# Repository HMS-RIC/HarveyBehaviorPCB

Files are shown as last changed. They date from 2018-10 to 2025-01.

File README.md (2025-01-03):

# HarveyBehaviorPCB v2
Circuit board for Harvey Lab VR behavior rigs

## Features
This board is designed to integrate a Teensy microcontroller and a National Instruments DAQ board (NI USB-600x) with the sensors and actuators on the behavior rig. Importantly, the board is used to convey the spherical treadmill movement signals to the VR computer. The Teensy makes a digital connection to the two ball movement sensors (mounted on the base of the spherical treadmill) to make continuous reading of ball movement. It then produces three analog outputs, representing velocity in the _Yaw_, _Pitch_, and _Roll_ axes, that are read into the VR computer by the DAQ board.

Other optional features of the PCB are: 
- Driver circuit for 2 solenoid valves (e.g. for liquid rewards)
- Two lick detector circuits
- A photodiode amplifier
- Many expansion ports/connectors: BNC connections, 0.1" headers, and a serial I2C connection (Qwiic connector)

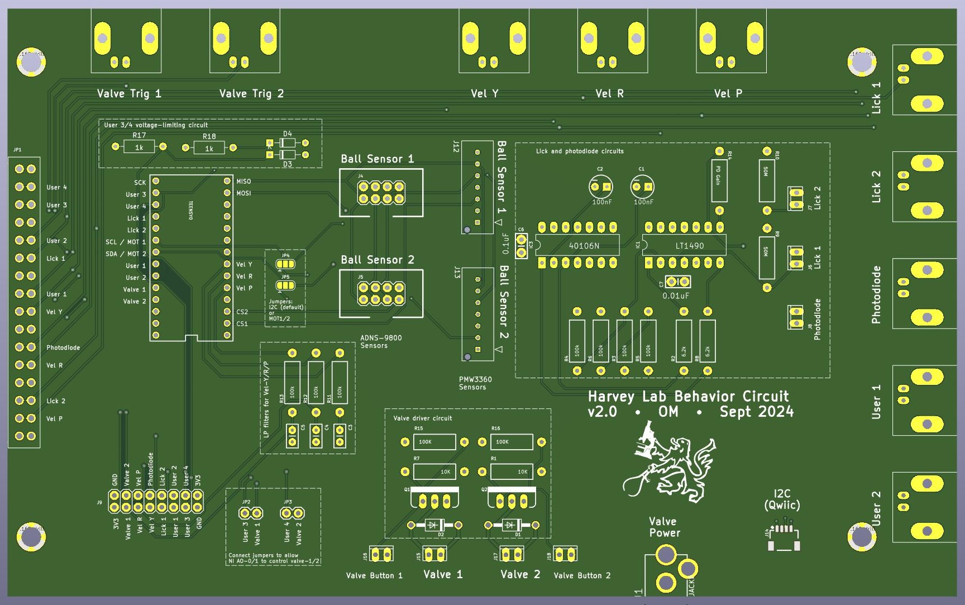
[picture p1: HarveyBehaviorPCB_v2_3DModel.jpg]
3D PCB model


## Fabrication
The full fabrication design is included in the [Gerber Zip File](PCB_v2_KiCAD/Gerbers/HarveyBehaviorPCB_v2.zip?raw=true). You can upload this file to any PCB fabricator to get a quote and place an order. (The board does not have any special features, so the default settings for PCB manufacture are probably fine.) One a relatively low-cost option for a board this size is the $33/board (3 board minimum) special at [Advanced Circuits](https://www.advancedpcb.com/en-us/33-each-special/).

## Assembly
The [Bill of Materials](HarveyBehaviorPCB_v2_BOM.xlsx?raw=true) (BOM) file has the full list of components. Everything but the optional I2C connector is a through-hole part and can be soldered on with a simple soldering iron (and [proper technique](https://mightyohm.com/files/soldercomic/FullSolderComic_EN.pdf)). The board is divided up into labeled regions that describe their high-level function and allow you to populate only the subset of components that you plan to use:
- **Ball sensor connectors**: The board is designed to work with two types of ball sensor ([ADNS-9800](https://www.tindie.com/products/citizenjoe/adns-9800-motion-sensor/) and [PMW3360](https://www.tindie.com/products/citizenjoe/pmw3360-motion-sensor/)). Chose one and populate the appropriate connector. (Also be sure to use the correct Teensy firmware for your ball sensor.)
- **Valve driver circuit**, **Lick and photodiode circuits**: These are optional functionalities. Only populate these regions if you plan to use them.
- **LP filters for velocity signals**: These are not optional. They low-pass filter the Teensy's digital (PWM) output to form a smooth analog signal for the NI board to acquire.
- **User 3/4 voltage-limiting circuit**: This is necessary if you plan to use the NI board's analog output pins (_AO-0_, _AO-1_) to control the voltage on _User-3_ and _User-4_. This circuit protects the Teensy from an accidental +5V output from the NI board (since the Teensy 4.0 cannot handle >3.3V inputs).
- **Jumpers JP2, JP3**: Optional. Short these jumpers (i.e., connect the pins within each jumper) to enable the NI analog output (_AO-0/1_, a.k.a. _User-3/4_) to control the valves.
- **Jumpers JP4, JP5**: Optional. In their default state they enable the I2C connector and disable the _MOT1_/_MOT2_ connections to the ball sensors. The _MOTx_ lines are not used during typical operation, so these jumpers are unlikely to be used.

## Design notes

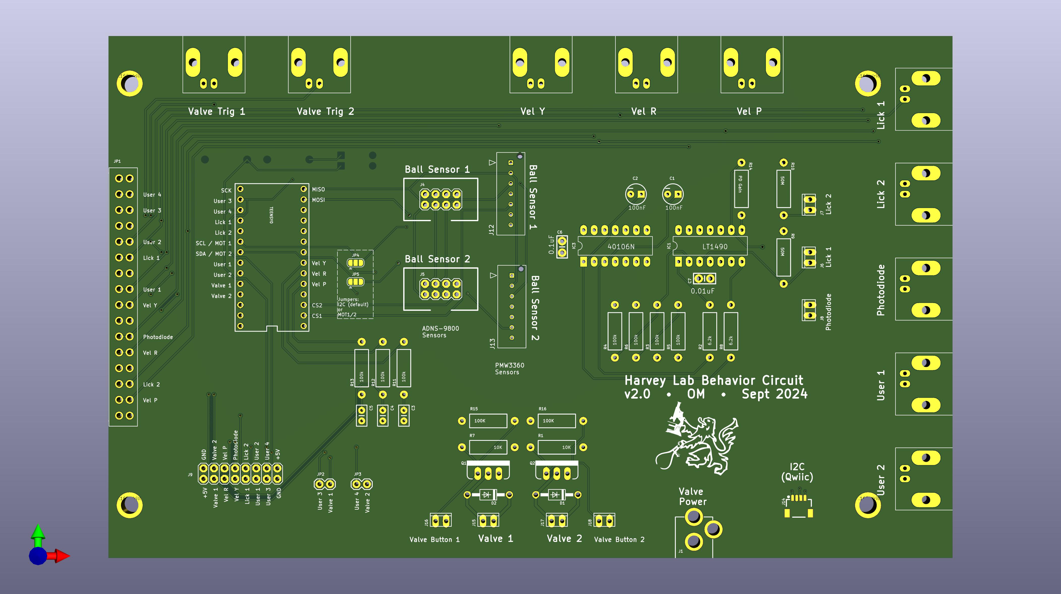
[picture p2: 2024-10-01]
PCB_v2_KiCAD/HarveyBehaviorPCB_v2.jpg

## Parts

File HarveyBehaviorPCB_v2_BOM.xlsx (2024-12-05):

Part | Value | Qty | Device | Digikey Part # | Unit Price | Total Price | Description | Notes
C1,C2 | 100nF | 2 |  |  |  | $0.00
C3-5 | 0.22uF | 3 |  |  |  | $0.00
C6 | 0.1uF | 1 |  |  |  | $0.00
C7 | 0.01uF | 1 |  |  |  | $0.00
D1,D2 | 1N4148 | 2 | Diode (1N58) | 497-7053-1-ND | $0.39 | $0.78
D3,D4 | Vz=3V3 | 2 | Zener diode, Vz=3.6V | 1727-6244-1-ND | $0.10 | $0.20
IC1 | LT1490A | 1 | LT1490A | LT1491ACN#PBF-ND | $6.41 | $6.41 | Quad OP AMP
IC3 | 40106N | 1 | 40106 | 296-3503-5-ND | $0.51 | $0.51 | Hex SCHMITT TRIGGER
J1 |  | 1 | PJ-202A | CP-202A-ND | $0.61 | $0.61
J4,J5 |  | 2 | Shrouded 2x4 header | 609-3530-ND | $0.76 | $1.52 | Connector to ADNS-9800 ball sensor | Pick only one connector type based on ball sensor model
J12,J13 |  | 2 | 1x7 connector | 900-0534760710-ND | $0.73 | $1.46 | Connector to PMW3360 ball sensor
J6-8,J15-18 | MTA02-100 | 7 | 1x2 connector | A19423-ND | $0.11 | $0.77 |  | Or any other 1x02 connector with 0.1" spacing
J9 | M08X2 | 1 | 2x8 header | 609-3220-ND | $0.60 | $0.60 |  | (or equivalent part)
J14 |  | 1 | JST SH/SR 4pos 1mm connector | 455-SM04B-SRSS-TBCT-ND | $0.71 | $0.71 | Qwiic/I2C Connector
JP1 | M16 | 1 | Connector to DAQ | 277-6221-ND | $17.34 | $17.34 | Connector to Ni USB-600x DAQ board
JP2,JP3 |  | 2 | JUMPER-2PTH | 952-2262-ND | $0.60 | $1.20 |  | also need jumper cap (e.g.,S9337-ND)
Q1,Q2 |  | 2 | nFET Transistor | 568-7512-5-ND | $2.20 | $4.40
R1,R7 | 10k | 2 | Standard (Axial) Resistor |  |  | $0.00
R2,R8 | 6.2k | 2 | Standard (Axial) Resistor |  |  | $0.00
R3-6, R11-13 | 100k | 7 | Standard (Axial) Resistor |  |  | $0.00
R9,R10 | 50M | 2 | Standard (Axial) Resistor |  |  | $0.00
R14 |  | 1 | Standard (Axial) Resistor |  |  | $0.00 |  | Chose value based on desired PD Gain
R15,R16 | 100K | 2 | Standard (Axial) Resistor |  |  | $0.00
R17,R18 | 1k | 2 | Standard (Axial) Resistor |  |  | $0.00
TEENSY0 |  | 1 | Teensy 3.2 or 4.0 |  |  | $0.00
U$1-10 |  | 10 | BNC Connector | WM5514-ND | $1.48 | $14.80
 |  |  | Additional conponents not on the PCB
 |  | 2 | Molex 0151370706 | WM25326-ND | $6.32 | $12.64 | Cable for PMW3360 ball sensor
 |  | 2 | Molex 0534260710 | WM14653-ND | $0.56 | $1.12 | Connector to be soldered to PMW3360 ball sensor

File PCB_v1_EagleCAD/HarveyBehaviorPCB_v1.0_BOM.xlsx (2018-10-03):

Part | Value | Device | Package | Description
C1 | 100nF
C2 | 100nF
C3 | 0.22uF
C4 | 0.22uF
C5 | 0.22uF
C6 | 0.1uF
C7 | 0.01uF
D1 | 1N4148 | 1N4004 |  | DIODE
D2 | 1N4148 | 1N4004 |  | DIODE
IC1 | LT1490A |  |  | Quad Wideband, Low Power Current Feedback OP AMP
IC3 | 40106N |  |  | Hex SCHMITT TRIGGER
J1 |  |  |  | Power Jack
J2 |  | M01SMTSO-256-ET-0.165DIA | SMTSO-256-ET-0.165DIA | Header 1
J3 |  | M01SMTSO-256-ET-0.165DIA | SMTSO-256-ET-0.165DIA | Header 1
J4 | BALL_1 | M04X2 | 2X4 | .1 header | two rows of four."
J5 | BALL_2 | M04X2 | 2X4 | .1 header | two rows of four."
J6 |  | MTA02-100 | 10X02MTA | AMP connector
J7 |  | MTA02-100 | 10X02MTA | AMP connector
J8 | Photodiode | MTA02-100 | 10X02MTA | AMP connector
J9 |  | M08X2 | 2X8 | .1 headers | two rows of 8 each"
J10 |  | M01SMTSO-256-ET-0.165DIA | SMTSO-256-ET-0.165DIA | Header 1
J11 |  | M01SMTSO-256-ET-0.165DIA | SMTSO-256-ET-0.165DIA | Header 1
J15 | Valve 1 | MTA02-100 | 10X02MTA | AMP connector
J16 | Valve 1 Switch | MTA02-100 | 10X02MTA | AMP connector
J17 | Valve 2 | MTA02-100 | 10X02MTA | AMP connector
J18 | Valve 2 Switch | MTA02-100 | 10X02MTA | AMP connector
JP1 | M16 | M16 | 1X16_TERM_BLOCK_0.15",1x16 .1" header"
Q1 | MOSFET-NCHANNELFQP30N06L |  | TO220V | Common NMOSFET Parts
Q2 | MOSFET-NCHANNELFQP30N06L |  | TO220V | Common NMOSFET Parts
R1 | 10K |  |  | Resistor
R2 | 6.2k |  |  | Resistor
R3 | 100k |  |  | Resistor
R4 | 100k |  |  | Resistor
R5 | 100k |  |  | Resistor
R6 | 100k |  |  | Resistor
R7 | 10K |  |  | Resistor
R8 | 6.2k |  |  | Resistor
R9 | 50M |  |  | Resistor
R10 | 50M |  |  | Resistor
R11 | 100k |  |  | Resistor
R12 | 100k |  |  | Resistor
R13 | 100k |  |  | Resistor
R14 | PD Gain |  |  | Resistor
TEENSY | TEENSY_3.1-3.2_DIL | TEENSY_3.1-3.2_DIL | TEENSY_3.0-3.2&LC_DIL | Teensy 3.1 or 3.2 in a DIL Layout.
U$1 | BNCPTH | BNCPTH | BNC | BNC Connector, Mouser Part# 5227161
U$2 | BNCPTH | BNCPTH | BNC | BNC Connector, Mouser Part# 5227161
U$3 | BNCPTH | BNCPTH | BNC | BNC Connector, Mouser Part# 5227161
U$4 | BNCPTH | BNCPTH | BNC | BNC Connector, Mouser Part# 5227161
U$5 | BNCPTH | BNCPTH | BNC | BNC Connector, Mouser Part# 5227161
U$6 | BNCPTH | BNCPTH | BNC | BNC Connector, Mouser Part# 5227161
U$7 | BNCPTH | BNCPTH | BNC | BNC Connector, Mouser Part# 5227161
U$8 | BNCPTH | BNCPTH | BNC | BNC Connector, Mouser Part# 5227161
U$9 | BNCPTH | BNCPTH | BNC | BNC Connector, Mouser Part# 5227161
U$10 | BNCPTH | BNCPTH | BNC | BNC Connector, Mouser Part# 5227161

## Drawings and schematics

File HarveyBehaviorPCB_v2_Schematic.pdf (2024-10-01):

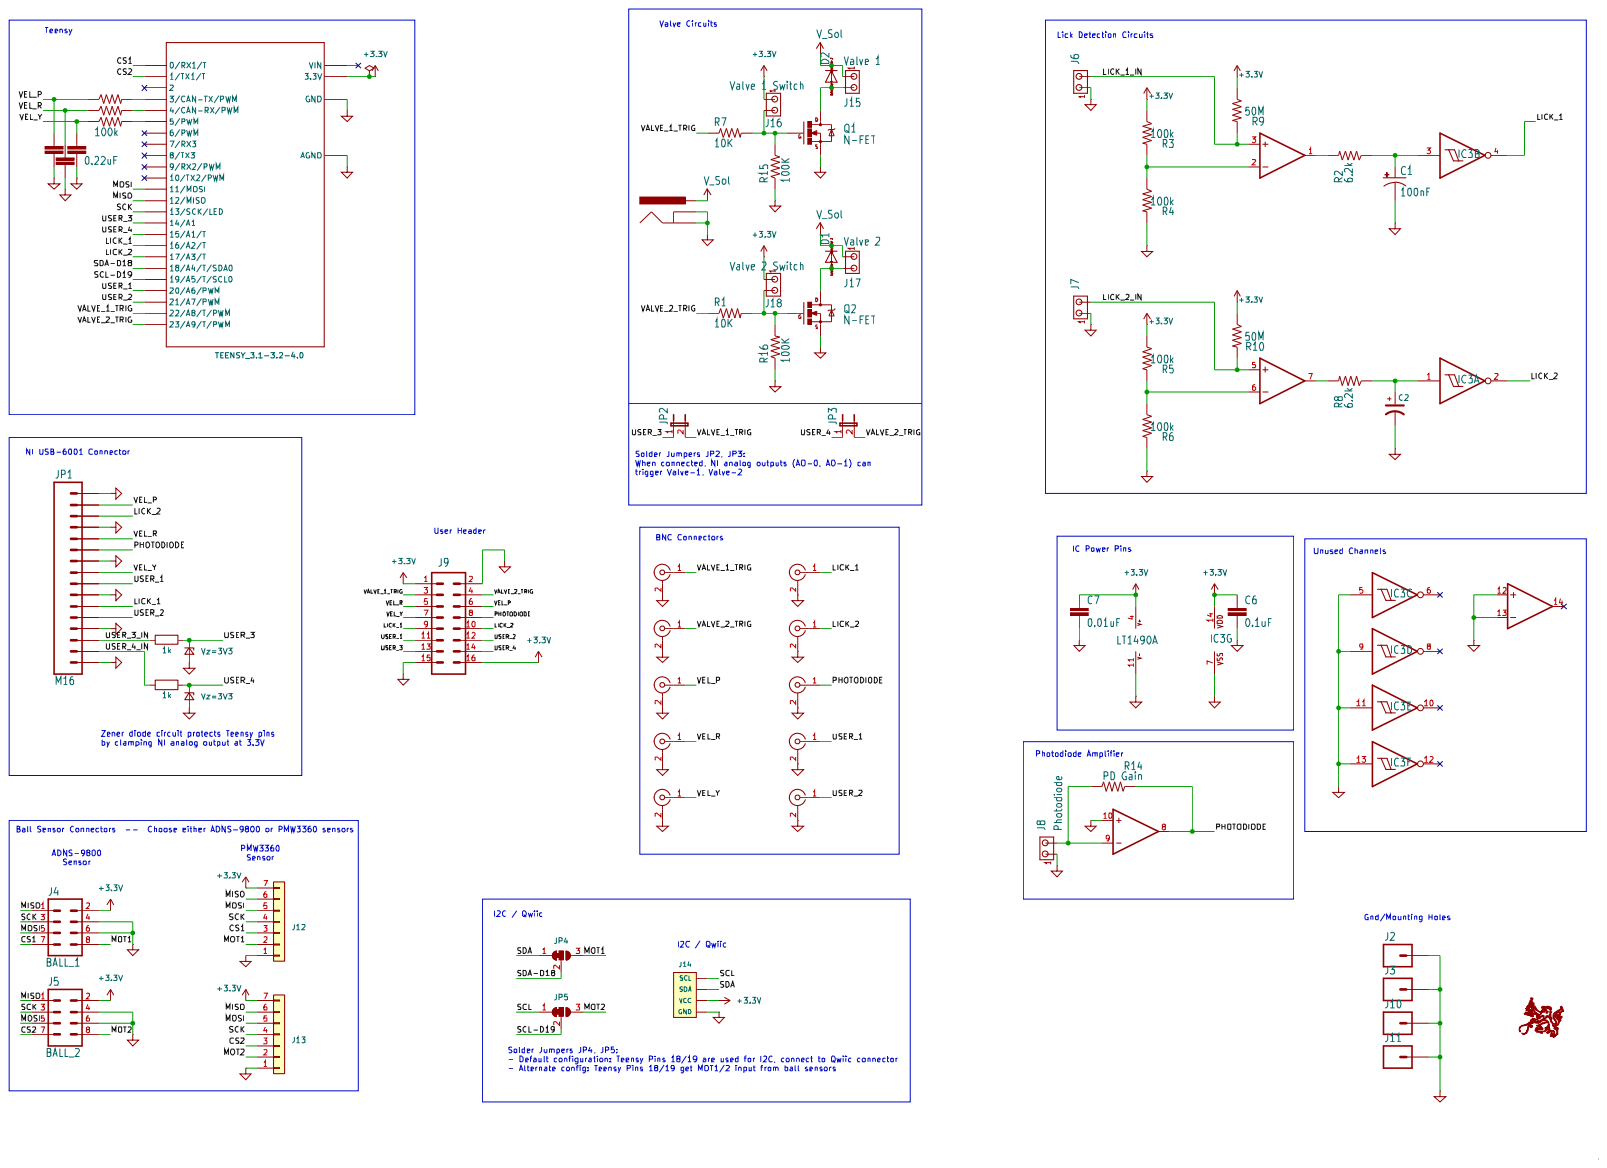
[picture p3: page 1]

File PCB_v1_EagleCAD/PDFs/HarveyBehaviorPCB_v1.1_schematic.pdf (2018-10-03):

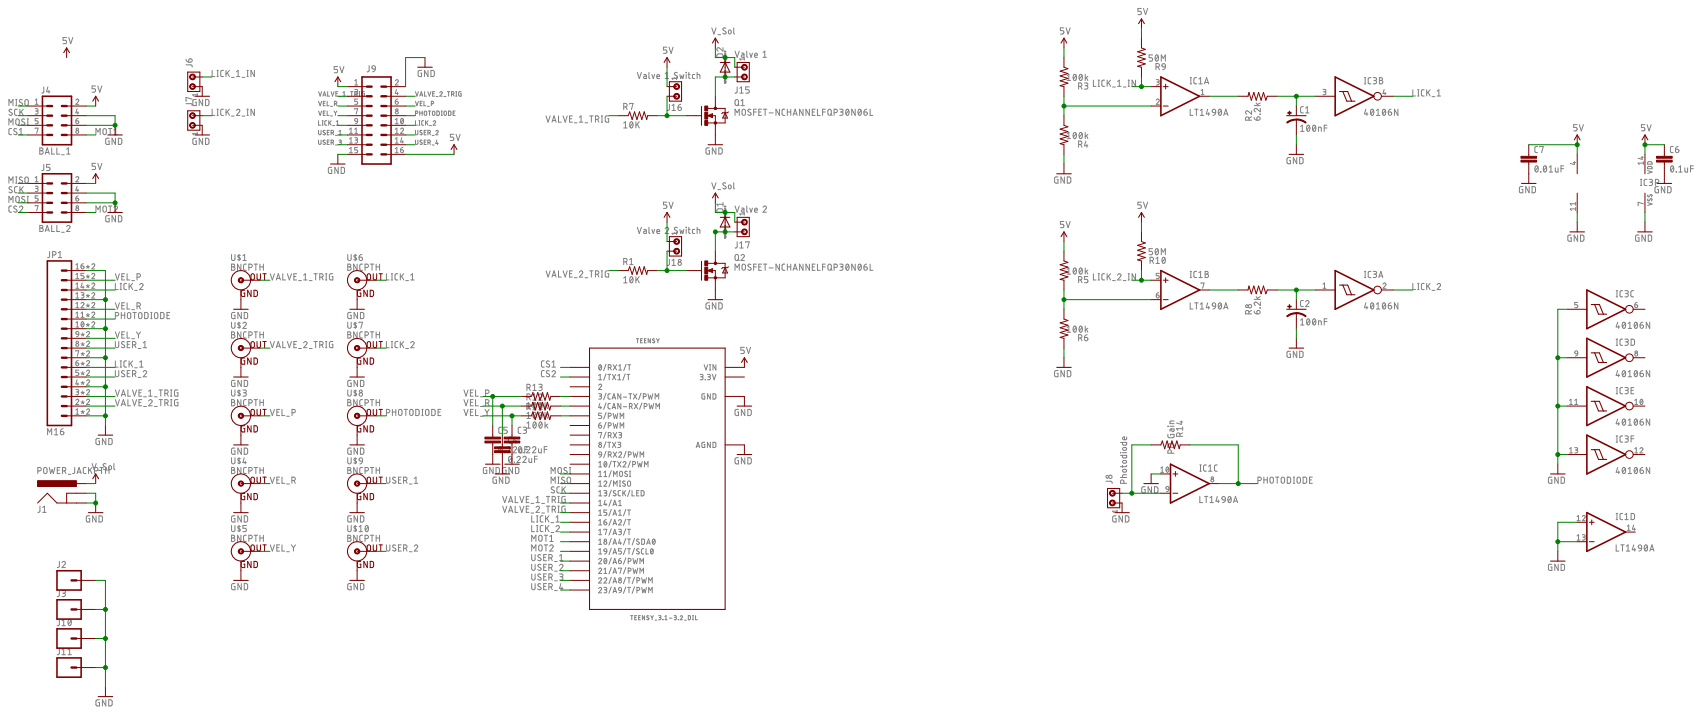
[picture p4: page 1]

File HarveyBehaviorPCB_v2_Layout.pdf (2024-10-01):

1 | 2 | 3 | 4 | 5

A

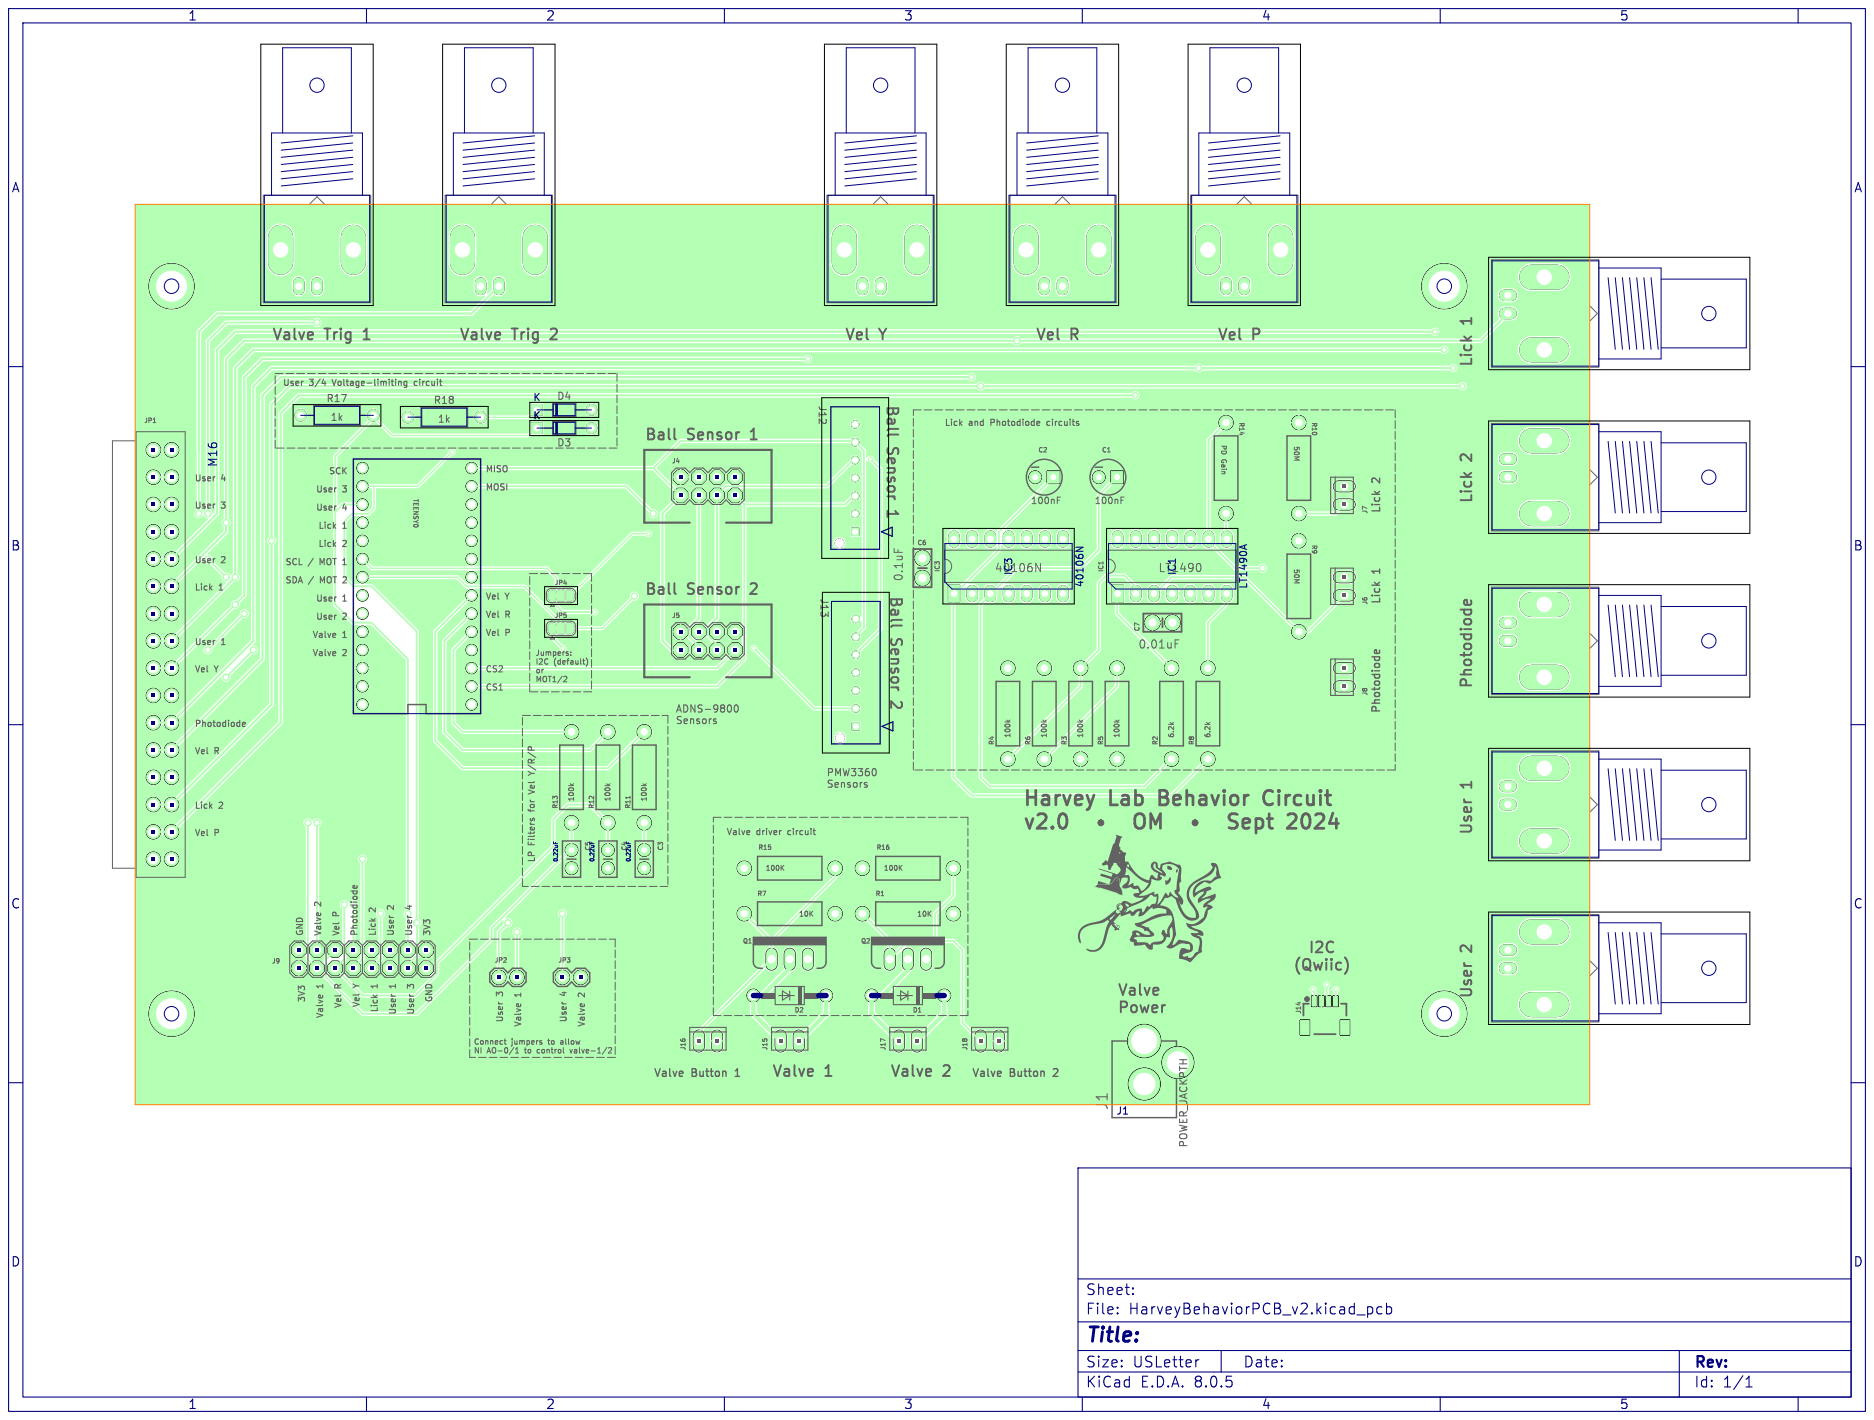
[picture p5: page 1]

Id: 1/1 Title: File: HarveyBehaviorPCB_v2.kicad_pcb Sheet:

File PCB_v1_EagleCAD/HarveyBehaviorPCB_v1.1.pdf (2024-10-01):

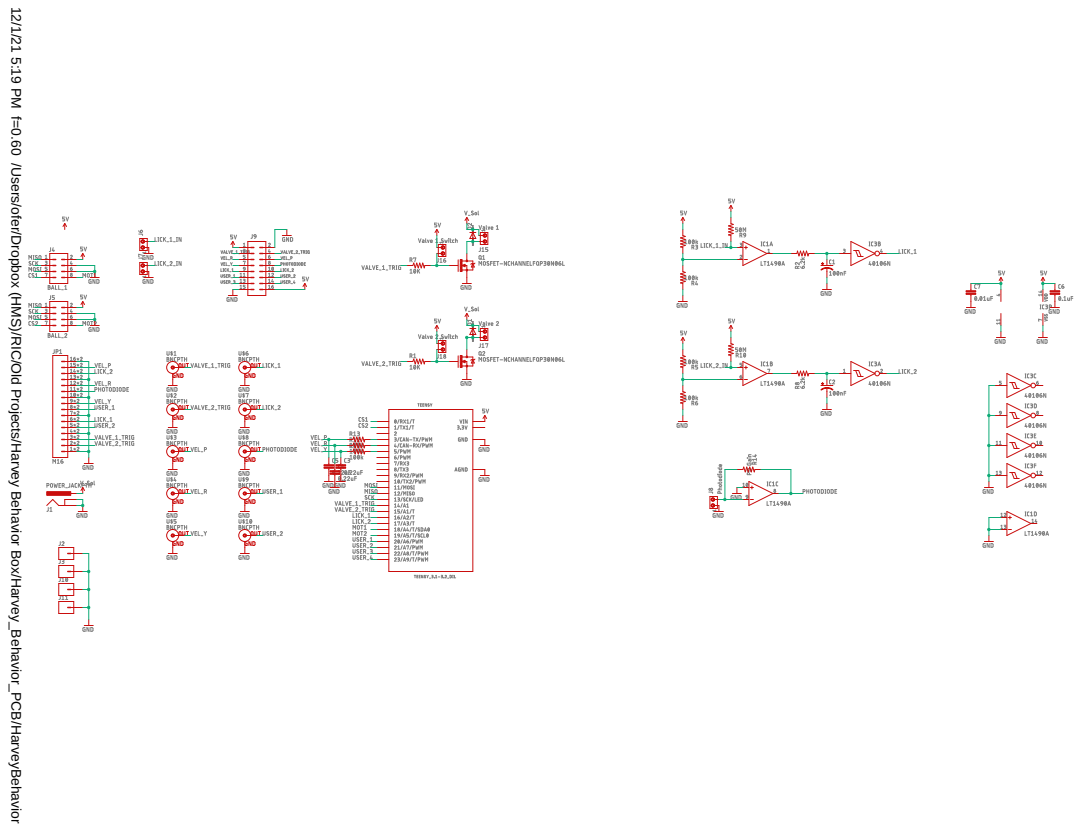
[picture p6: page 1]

12/1/21 5:19 PM f=0.60 /Users/ofer/Dropbox (HMS)/RIC/Old Projects/Harvey Behavior Box/Harvey_Behavior_PCB/HarveyBehaviorPCB_v1.1.sch (Sheet: 1/1)

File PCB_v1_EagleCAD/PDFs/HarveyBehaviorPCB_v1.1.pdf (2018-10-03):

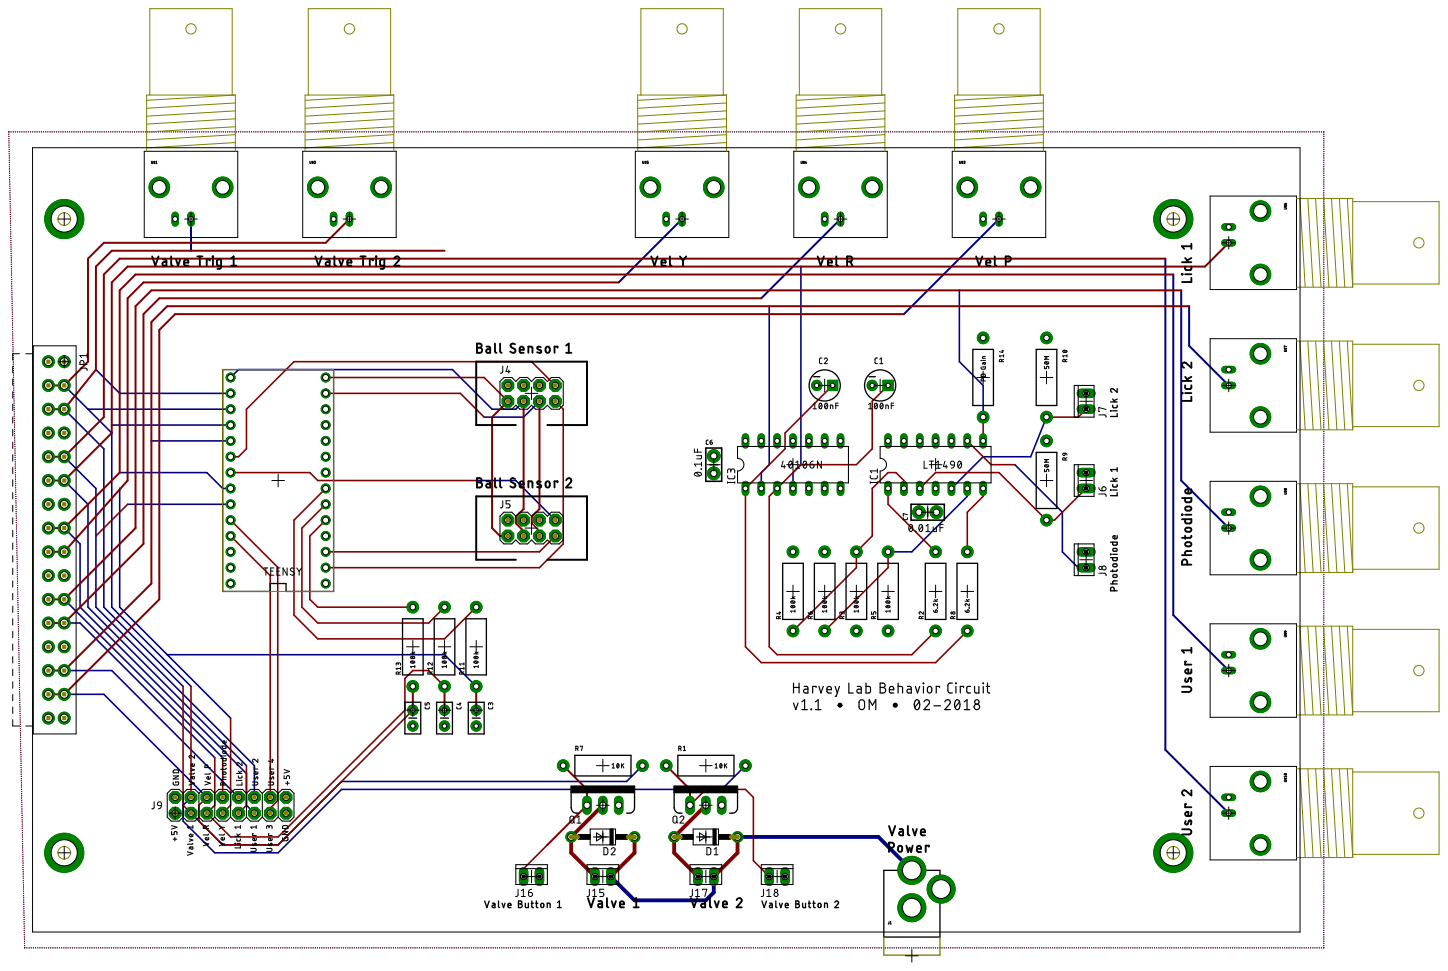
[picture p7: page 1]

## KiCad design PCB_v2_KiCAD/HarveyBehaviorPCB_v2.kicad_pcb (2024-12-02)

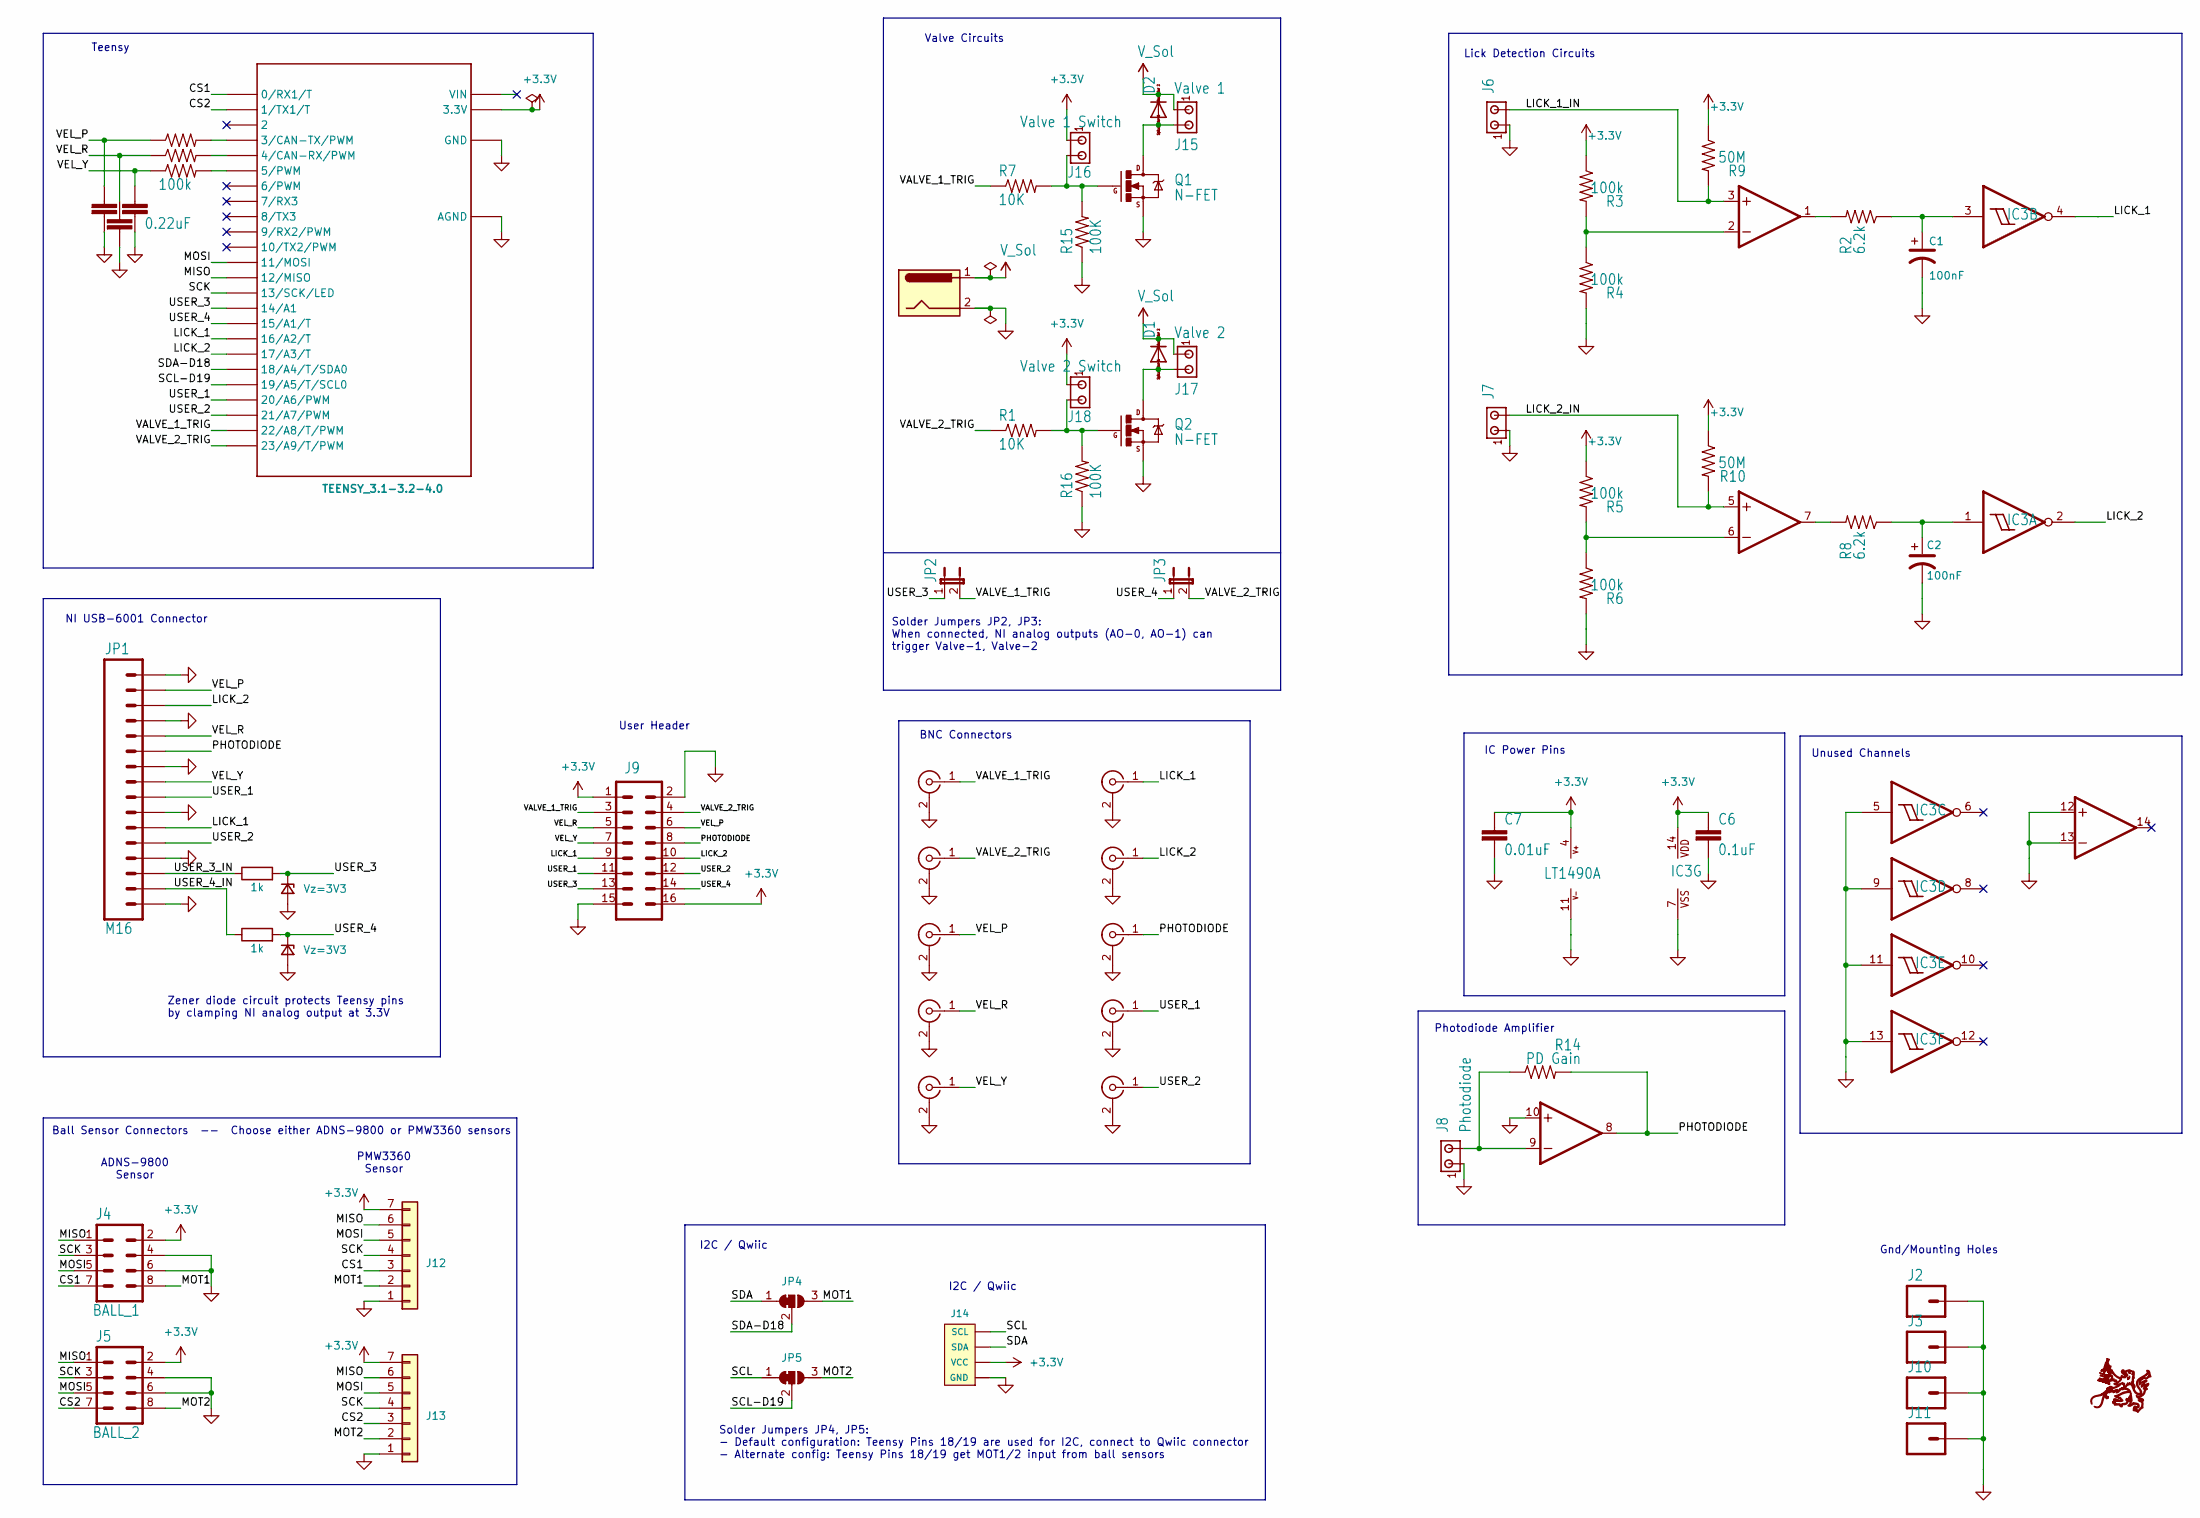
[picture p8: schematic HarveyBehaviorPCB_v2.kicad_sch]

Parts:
C1, C2: 100nF; CPOL-RADIAL-10UF-25V
C3, C4, C5: 0.22uF; CAP-PTH-SMALL2
C6: 0.1uF; CAP-PTH-SMALL-KIT
C7: 0.01uF; CAP-PTH-SMALL-KIT
D1, D2: 1N4148; DO41-10
D3, D4: Vz=3V3; D_DO-34_SOD68_P7.62mm_Horizontal
IC1: LT1490A; DIP-14_W7.62mm_LongPads
IC3: 40106N; DIP-14_W7.62mm_LongPads
J1: POWER_JACKPTH; POWER_JACK_PTH
J2, J3, J10, J11: M01SMTSO-256-ET-0.165DIA; SMTSO-256-ET-0.165DIA
J4: BALL_1; 2X4
J5: BALL_2; 2X4
J6, J7: MTA02-100; 10X02MTA
J8: Photodiode; 10X02MTA
J9: M08X2; 2X8
J12, J13: Conn_01x07; CON_535170730_MOL
J14: I2C_STANDARDQWIIC; 1X04_1MM_RA
J15: Valve 1; 10X02MTA
J16: Valve 1 Switch; 10X02MTA
J17: Valve 2; 10X02MTA
J18: Valve 2 Switch; 10X02MTA
JP1: M16; 1X16_TERM_BLOCK_0.15_
JP2, JP3: JUMPER-2PTH; 1X02
JP4, JP5: SolderJumper_3_Bridged12; SolderJumper-3_P1.3mm_Bridged12_RoundedPad1.0x1.5mm
Q1, Q2: N-FET; TO220V
R1, R7: 10K; AXIAL-0.5
R2, R8: 6.2k; AXIAL-0.5
R3, R4, R5, R6, R11, R12, R13: 100k; AXIAL-0.5
R9, R10: 50M; AXIAL-0.5
R14: PD Gain; AXIAL-0.5
R15, R16: 100K; AXIAL-0.5
R17, R18: 1k; R_Axial_DIN0207_L6.3mm_D2.5mm_P10.16mm_Horizontal
TEENSY0: TEENSY_3.1-3.2-4.0; TEENSY_3.0-3.2&LC_DIL
U$1, U$2, U$3, U$4, U$5, U$6, U$7, U$8, U$9, U$10: BNCPTH; BNC_Amphenol_B6252HB-NPP3G-50_Horizontal

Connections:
+3.3V: C6.1, C7.1, IC1.4 (V+), IC3.14 (VDD), J4.2, J5.2, J9.1, J9.16, J12.7, J13.7, J14.2 (VCC), J16.1, J18.1, R3.P$1 (1), R5.P$1 (1), R9.P$1 (1), R10.P$1 (1), TEENSY0.3.3V
/CS1: J4.7, J12.3, TEENSY0.0 (0/RX1/T)
/CS2: J5.7, J13.3, TEENSY0.1 (1/TX1/T)
/LICK_1: IC3.4 (O), J9.9, JP1.6, JP1.22 (6), TEENSY0.16/A2 (16/A2/T), U$6.1 (In)
/LICK_1_IN: IC1.3 (+IN), J6.2, R9.P$2 (2)
/LICK_2: IC3.2 (O), J9.10, JP1.14, JP1.30 (14), TEENSY0.17/A3 (17/A3/T), U$7.1 (In)
/LICK_2_IN: IC1.5 (+IN), J7.2, R10.P$2 (2)
/MISO: J4.1, J5.1, J12.6, J13.6, TEENSY0.12 (12/MISO)
/MOSI: J4.5, J5.5, J12.5, J13.5, TEENSY0.11 (11/MOSI)
/MOT1: J4.8, J12.2, JP4.3 (B)
/MOT2: J5.8, J13.2, JP5.3 (B)
/PHOTODIODE: IC1.8 (OUT), J9.8, JP1.11, JP1.27 (11), R14.P$2 (2), U$8.1 (In)
/SCK: J4.3, J5.3, J12.4, J13.4, TEENSY0.13 (13/SCK/LED)
/SCL: J14.4 (SCL), JP5.1 (A)
/SCL-D19: JP5.2 (C), TEENSY0.19/A5 (19/A5/T/SCL0)
/SDA: J14.3 (SDA), JP4.1 (A)
/SDA-D18: JP4.2 (C), TEENSY0.18/A4 (18/A4/T/SDA0)
/USER_1: J9.11, JP1.8, JP1.24 (8), TEENSY0.20/A6 (20/A6/PWM), U$9.1 (In)
/USER_2: J9.12, JP1.5, JP1.21 (5), TEENSY0.21/A7 (21/A7/PWM), U$10.1 (In)
/USER_3: D4.1 (K), J9.13, JP2.1, R18.2, TEENSY0.14/A0 (14/A1)
/USER_3_IN: JP1.3, JP1.19 (3), R18.1
/USER_4: D3.1 (K), J9.14, JP3.1, R17.2, TEENSY0.15/A1 (15/A1/T)
/USER_4_IN: JP1.2, JP1.18 (2), R17.1
/VALVE_1_TRIG: J9.3, JP2.2, R7.P$1 (1), TEENSY0.22/A8 (22/A8/T/PWM), U$1.1 (In)
/VALVE_2_TRIG: J9.4, JP3.2, R1.P$1 (1), TEENSY0.23/A9 (23/A9/T/PWM), U$2.1 (In)
/VEL_P: C5.1, J9.6, JP1.15, JP1.31 (15), R13.P$1 (1), U$3.1 (In)
/VEL_R: C4.1, J9.5, JP1.12, JP1.28 (12), R12.P$1 (1), U$4.1 (In)
/VEL_Y: C3.1, J9.7, JP1.9, JP1.25 (9), R11.P$1 (1), U$5.1 (In)
GND: C1.2 (-), C2.2, C3.2, C4.2, C5.2, C6.2, C7.2, D3.2 (A), D4.2 (A), IC1.10 (+IN), IC1.11 (V-), IC1.12 (+IN), IC1.13 (-IN), IC3.5 (I), IC3.7 (VSS), IC3.9 (I), IC3.11 (I), IC3.13 (I), J1.2, J2.P$1 (1), J3.P$1 (1), J4.4, J4.6, J5.4, J5.6, J6.1, J7.1, J8.1, J9.2, J9.15, J10.P$1 (1), J11.P$1 (1), J12.1, J13.1, J14.1 (GND), JP1.1, JP1.4, JP1.7, JP1.10, JP1.13, JP1.16, JP1.17 (1), JP1.20 (4), JP1.23 (7), JP1.26 (10), JP1.29 (13), JP1.32 (16), Q1.3 (S), Q2.3 (S), R4.P$2 (2), R6.P$2 (2), R15.P$1 (1), R16.P$1 (1), TEENSY0.AGND, TEENSY0.GND, U$1.2 (Ext), U$2.2 (Ext), U$3.2 (Ext), U$4.2 (Ext), U$5.2 (Ext), U$6.2 (Ext), U$7.2 (Ext), U$8.2 (Ext), U$9.2 (Ext), U$10.2 (Ext)
unnamed: C1.1 (+), IC3.3 (I), R2.P$1 (1)
unnamed: IC1.2 (-IN), R3.P$2 (2), R4.P$1 (1)
unnamed: IC1.1 (OUT), R2.P$2 (2)
unnamed: IC1.6 (-IN), R5.P$2 (2), R6.P$1 (1)
unnamed: IC1.7 (OUT), R8.P$2 (2)
unnamed: IC1.9 (-IN), J8.2, R14.P$1 (1)
unnamed: C2.1, IC3.1 (I), R8.P$1 (1)
unnamed: D2.A, J15.2, Q1.2 (D)
unnamed: J16.2, Q1.1 (G), R7.P$2 (2), R15.P$2 (2)
unnamed: D1.A, J17.2, Q2.2 (D)
unnamed: J18.2, Q2.1 (G), R1.P$2 (2), R16.P$2 (2)
unnamed: R11.P$2 (2), TEENSY0.5 (5/PWM)
unnamed: R12.P$2 (2), TEENSY0.4 (4/CAN-RX/PWM)
unnamed: R13.P$2 (2), TEENSY0.3 (3/CAN-TX/PWM)
V_Sol: D1.C, D2.C, J1.1, J15.1, J17.1

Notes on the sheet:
NI USB-6001 Connector
Zener diode circuit protects Teensy pins by clamping NI analog output at 3.3V
BNC Connectors
Lick Detection Circuits
I2C / Qwiic
Photodiode Amplifier
Valve Circuits
Gnd/Mounting Holes
User Header
ADNS-9800 Sensor
Solder Jumpers JP4, JP5: - Default configuration: Teensy Pins 18/19 are used for I2C, connect to Qwiic connector - Alternate config: Teensy Pins 18/19 get MOT1/2 input from ball sensors
IC Power Pins
Teensy
Solder Jumpers JP2, JP3: When connected, NI analog outputs (AO-0, AO-1) can trigger Valve-1, Valve-2
Unused Channels
PMW3360 Sensor
Ball Sensor Connectors -- Choose either ADNS-9800 or PMW3360 sensors

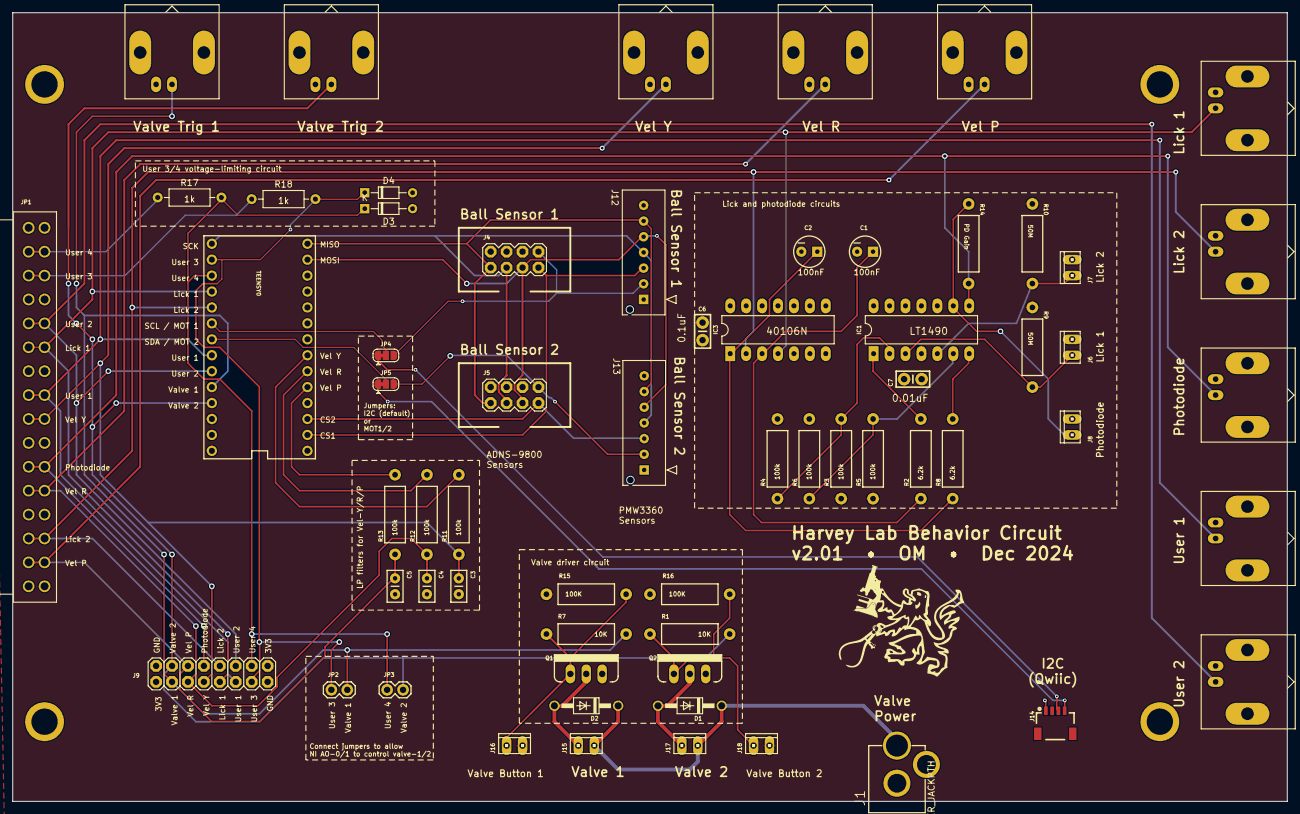
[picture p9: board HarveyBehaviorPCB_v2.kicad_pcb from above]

Board: 2 copper layers, 203.2 x 125.7 mm, 67 parts (0 on the bottom side), 44 nets.

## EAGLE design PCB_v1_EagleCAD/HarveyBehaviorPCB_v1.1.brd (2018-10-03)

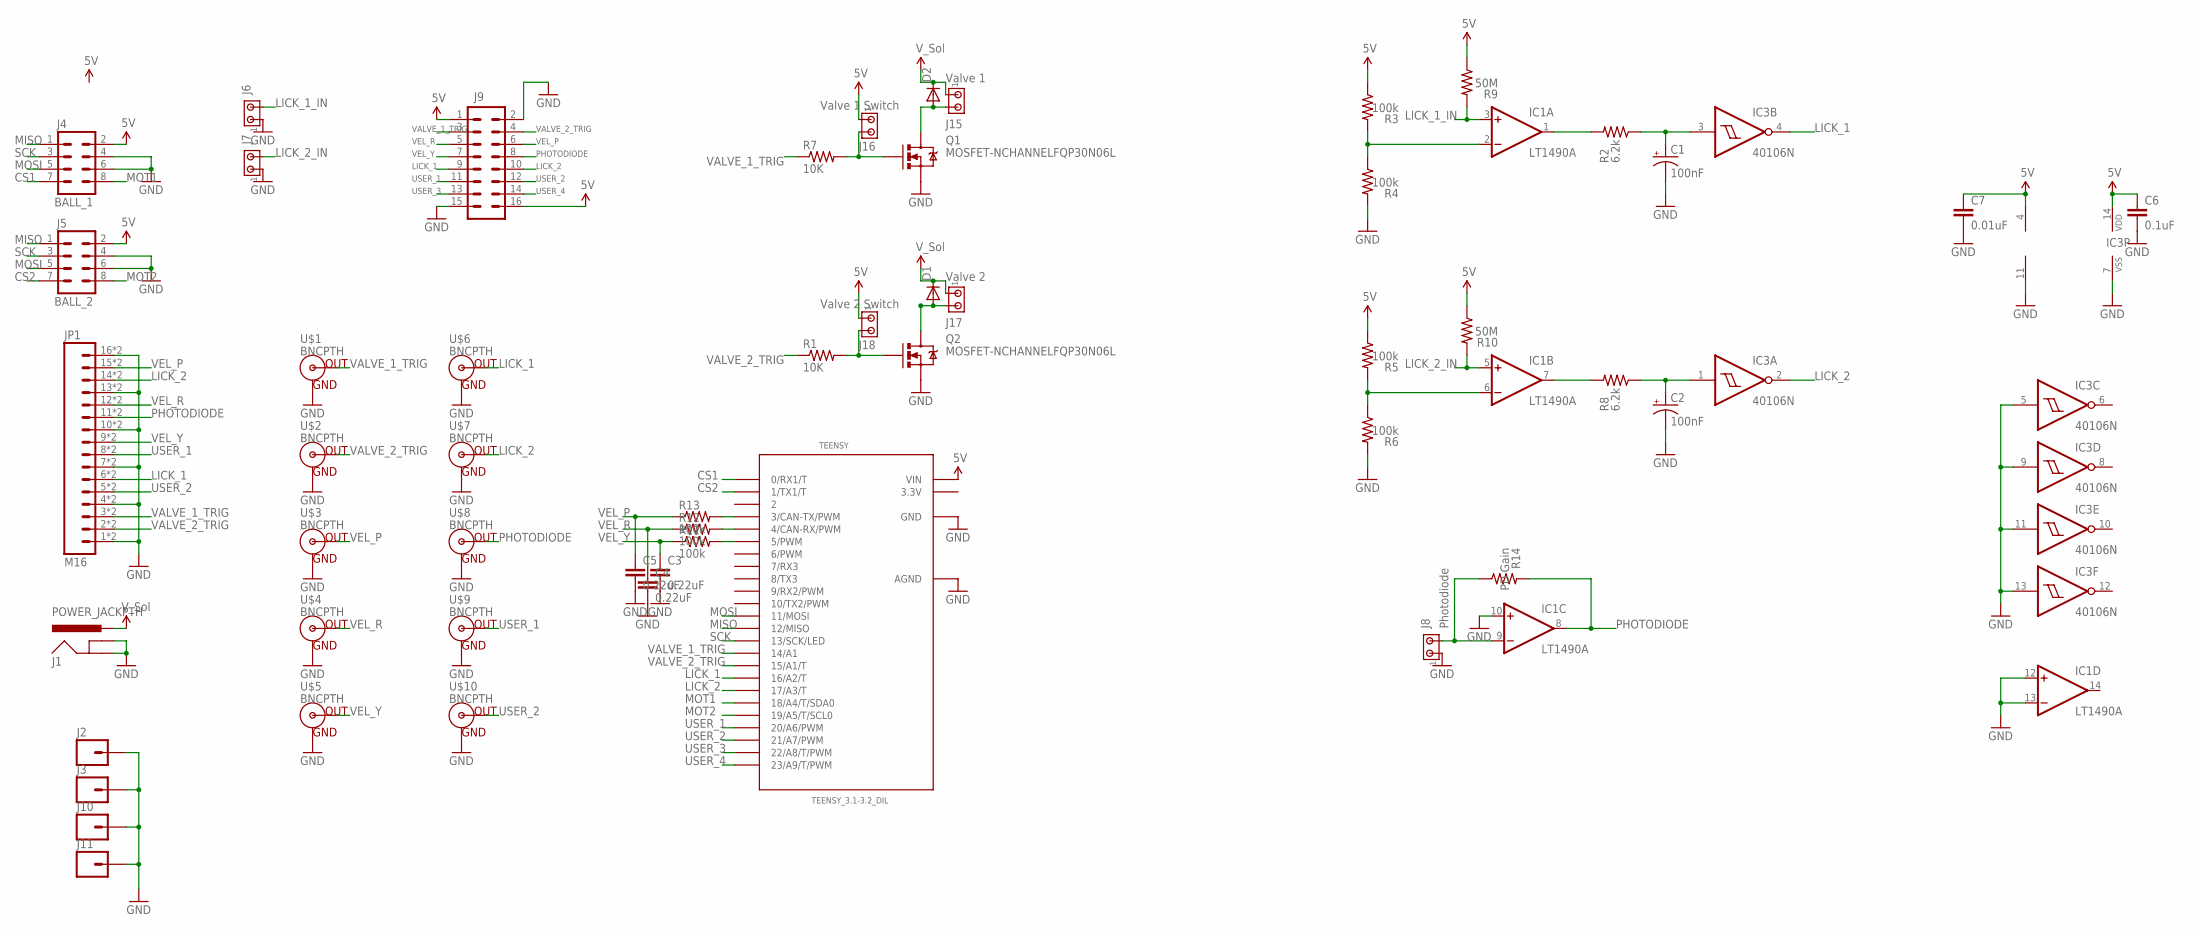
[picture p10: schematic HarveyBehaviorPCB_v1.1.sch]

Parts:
C1, C2: 100nF; CPOL-RADIAL-10UF-25V
C3, C4, C5: 0.22uF; CAP-PTH-SMALL2
C6: 0.1uF; CAP-PTH-SMALL-KIT
C7: 0.01uF; CAP-PTH-SMALL-KIT
D1, D2: 1N4148; DO41-10
IC1: LT1490A; DIL14
IC3: 40106N; DIL14
J1: POWER_JACKPTH; POWER_JACK_PTH
J2, J3, J10, J11: M01SMTSO-256-ET-0.165DIA; SMTSO-256-ET-0.165DIA
J4: BALL_1; 2X4
J5: BALL_2; 2X4
J6, J7: MTA02-100; 10X02MTA
J8: Photodiode; 10X02MTA
J9: M08X2; 2X8
J15: Valve 1; 10X02MTA
J16: Valve 1 Switch; 10X02MTA
J17: Valve 2; 10X02MTA
J18: Valve 2 Switch; 10X02MTA
JP1: M16; 1X16_TERM_BLOCK_0.15"
Q1, Q2: MOSFET-NCHANNELFQP30N06L; TO220V
R1, R7: 10K; AXIAL-0.5
R2, R8: 6.2k; AXIAL-0.5
R3, R4, R5, R6, R11, R12, R13: 100k; AXIAL-0.5
R9, R10: 50M; AXIAL-0.5
R14: PD Gain; AXIAL-0.5
TEENSY: TEENSY_3.1-3.2_DIL; TEENSY_3.0-3.2&LC_DIL
U$1, U$2, U$3, U$4, U$5, U$6, U$7, U$8, U$9, U$10: BNCPTH; BNC

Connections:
3.3V: TEENSY.3.3V
5V: C6.1, C7.1, IC1.4 (V+), IC3.14 (VDD), J4.2, J5.2, J9.1, J9.16, J16.1, J18.1, R3.P$1 (1), R5.P$1 (1), R9.P$1 (1), R10.P$1 (1), TEENSY.VIN
CS1: J4.7, TEENSY.0 (0/RX1/T)
CS2: J5.7, TEENSY.1 (1/TX1/T)
GND: C1.2 (-), C2.2 (-), C3.2, C4.2, C5.2, C6.2, C7.2, IC1.10 (+IN), IC1.11 (V-), IC1.12 (+IN), IC1.13 (-IN), IC3.5 (I), IC3.7 (VSS), IC3.9 (I), IC3.11 (I), IC3.13 (I), J1.GND, J1.GNDBREAK, J2.P$1, J3.P$1, J4.4, J4.6, J5.4, J5.6, J6.1, J7.1, J8.1, J9.2, J9.15, J10.P$1, J11.P$1, JP1.1, JP1.4, JP1.7, JP1.10, JP1.13, JP1.16, JP1.17 (1), JP1.20 (4), JP1.23 (7), JP1.26 (10), JP1.29 (13), JP1.32 (16), Q1.3 (S), Q2.3 (S), R4.P$2 (2), R6.P$2 (2), TEENSY.AGND, TEENSY.GND, U$1.GND, U$2.GND, U$3.GND, U$4.GND, U$5.GND, U$6.GND, U$7.GND, U$8.GND, U$9.GND, U$10.GND
LICK_1: IC3.4 (O), J9.9, JP1.6, JP1.22 (6), TEENSY.16/A2 (16/A2/T), U$6.S (OUT)
LICK_1_IN: IC1.3 (+IN), J6.2, R9.P$2 (2)
LICK_2: IC3.2 (O), J9.10, JP1.14, JP1.30 (14), TEENSY.17/A3 (17/A3/T), U$7.S (OUT)
LICK_2_IN: IC1.5 (+IN), J7.2, R10.P$2 (2)
MISO: J4.1, J5.1, TEENSY.12 (12/MISO)
MOSI: J4.5, J5.5, TEENSY.11 (11/MOSI)
MOT1: J4.8, TEENSY.18/A4 (18/A4/T/SDA0)
MOT2: J5.8, TEENSY.19/A5 (19/A5/T/SCL0)
unnamed: C1.1 (+), IC3.3 (I), R2.P$1 (1)
unnamed: IC1.1 (OUT), R2.P$2 (2)
unnamed: IC1.2 (-IN), R3.P$2 (2), R4.P$1 (1)
unnamed: D2.A, J15.2, Q1.2 (D)
unnamed: J16.2, Q1.1 (G), R7.P$2 (2)
unnamed: D1.A, J17.2, Q2.2 (D)
unnamed: J18.2, Q2.1 (G), R1.P$2 (2)
unnamed: IC1.6 (-IN), R5.P$2 (2), R6.P$1 (1)
unnamed: C2.1 (+), IC3.1 (I), R8.P$1 (1)
unnamed: IC1.7 (OUT), R8.P$2 (2)
PHOTODIODE: IC1.8 (OUT), J9.8, JP1.11, JP1.27 (11), R14.P$2 (2), U$8.S (OUT)
PHOTODIODE_IN: IC1.9 (-IN), J8.2
SCK: J4.3, J5.3, TEENSY.13 (13/SCK/LED)
USER_1: J9.11, JP1.8, JP1.24 (8), TEENSY.20/A6 (20/A6/PWM), U$9.S (OUT)
USER_2: J9.12, JP1.5, JP1.21 (5), TEENSY.21/A7 (21/A7/PWM), U$10.S (OUT)
USER_3: J9.13, TEENSY.22/A8 (22/A8/T/PWM)
USER_4: J9.14, TEENSY.23/A9 (23/A9/T/PWM)
VALVE_1_TRIG: J9.3, JP1.3, JP1.19 (3), R7.P$1 (1), TEENSY.14/A0 (14/A1), U$1.S (OUT)
VALVE_2_TRIG: J9.4, JP1.2, JP1.18 (2), R1.P$1 (1), TEENSY.15/A1 (15/A1/T), U$2.S (OUT)
VEL_P: C5.1, J9.6, JP1.15, JP1.31 (15), R13.P$1 (1), U$3.S (OUT)
VEL_P_PWM: R13.P$2 (2), TEENSY.3 (3/CAN-TX/PWM)
VEL_R: C4.1, J9.5, JP1.12, JP1.28 (12), R12.P$1 (1), U$4.S (OUT)
VEL_R_PWM: R12.P$2 (2), TEENSY.4 (4/CAN-RX/PWM)
VEL_Y: C3.1, J9.7, JP1.9, JP1.25 (9), R11.P$1 (1), U$5.S (OUT)
VEL_Y_PWM: R11.P$2 (2), TEENSY.5 (5/PWM)
VSOL: D1.C, D2.C, J1.PWR, J15.1, J17.1

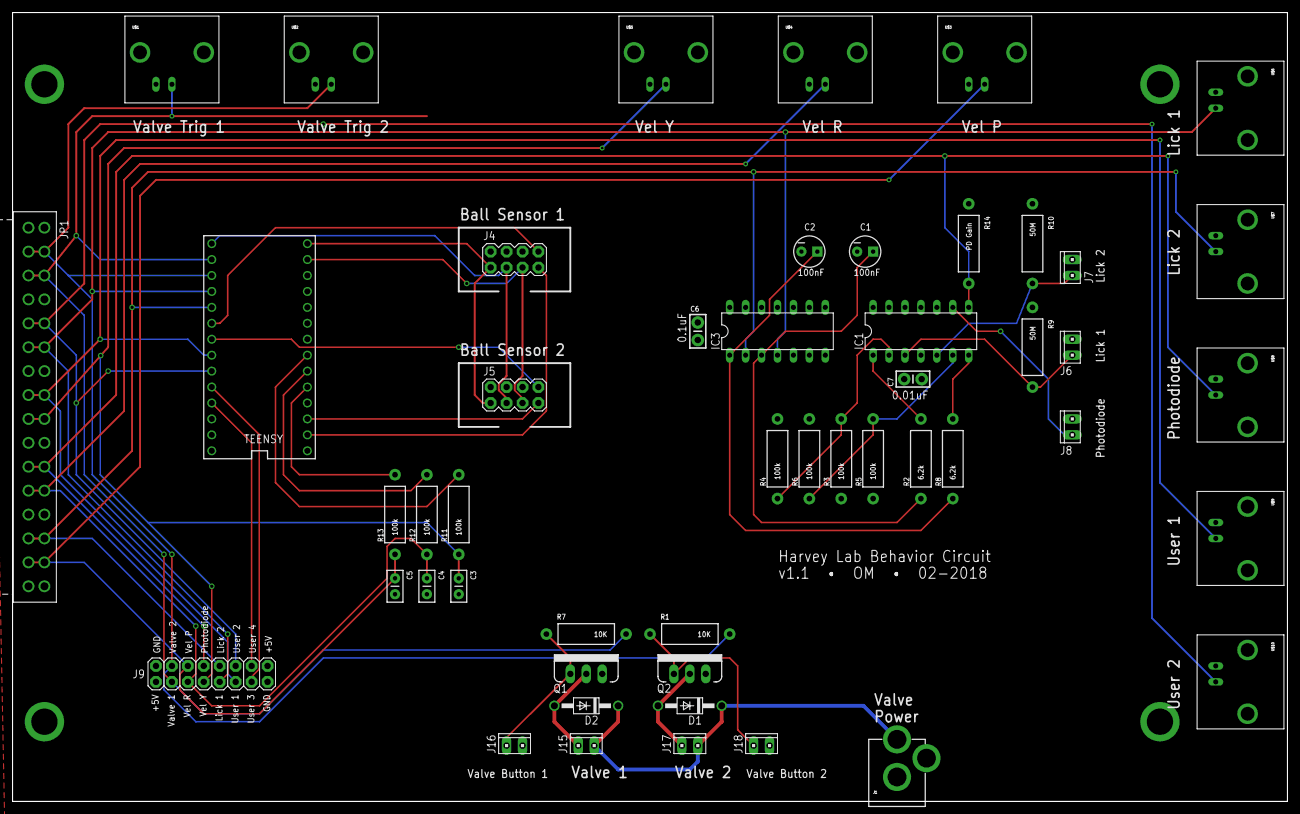
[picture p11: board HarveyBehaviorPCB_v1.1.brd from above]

Board: 2 copper layers, 203.2 x 125.7 mm, 54 parts (0 on the bottom side), 38 nets.

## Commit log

2018-10-03 initial commit (v1.2)
    [.GBL, .GBS, .GTL, .GTO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]
2018-10-03 Rename some files
    [HarveyBehaviorPCB_v1.0.brd, HarveyBehaviorPCB_v1.0.sch]
2024-10-01 Convert to KiCad and update design to v2.0
    [.GBL, .GBS, .GTL, .GTO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]
2024-10-07 Make Gerbers for v2.0
    [HarveyBehaviorPCB_v2-B_Cu.gbr, HarveyBehaviorPCB_v2-B_Mask.gbr, HarveyBehaviorPCB_v2-B_Paste.gbr, HarveyBehaviorPCB_v2-B_Silkscreen.gbr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]
2024-11-08 Update .gitignore; Add datasheet for ball sensor cable
2024-11-08 Rearrange files
    [HarveyBehaviorPCB_v2_BOM.xlsx]
2024-11-27 Update BOM for v2.0
    [HarveyBehaviorPCB_v2.kicad_sch, HarveyBehaviorPCB_v2_BOM.xlsx]
2024-11-27 Update PCB render
2024-12-02 [PCB] Increase width of copper pads on a few footprints; v2.0 -> v2.01
    [HarveyBehaviorPCB_v2.kicad_pcb]
2024-12-05 Update BOM
    [HarveyBehaviorPCB_v2_BOM.xlsx]

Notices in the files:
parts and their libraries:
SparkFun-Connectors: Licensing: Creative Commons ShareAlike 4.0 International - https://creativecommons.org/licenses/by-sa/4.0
